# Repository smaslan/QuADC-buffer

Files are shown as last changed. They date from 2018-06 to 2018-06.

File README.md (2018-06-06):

# Precision Buffer with Low Input Capacitance

Following project is a precision buffer developed in scope of project EMPIR project QuADC (see documentation.pdf for details).

The main goal was flatness below 0.1 µV/V up to 10 kHz. Calibration uncertainty at 1 MHz requirement was 5 µV/V. Input capacitance as low as possible. Output impedance as low as possible. The circuit uses bootstrapping of the supply voltages which reduces errors significantly and also ensure very low apparent input shunting capacitance. Cost for the solution is limited stability. The buffer cannot be supplied from low impedance source otherwise it tends to oscillate. It designed as output bufffer for the resistive voltage dividers.

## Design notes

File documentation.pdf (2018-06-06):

## Report on the bootstrapped buffer for QuADC EMPIR

V1.1, 2018-06-06, Czech Metrology Institute, Stanislav Mašláň, smaslan@cmi, s.maslan@seznam.cz

Copyright 2017, Stanislav Mašláň.

This documentation describes Open Hardware and is licensed under the CERN OHL v. 1.2. You may redistribute and modify this documentation under the terms of the CERN OHL v.1.2. (http://ohwr.org/cernohl). This documentation is distributed WITHOUT ANY EXPRESS OR IMPLIED WARRANTY, INCLUDING OF MERCHANTABILITY, SATISFACTORY QUALITY AND FITNESS FOR A PARTICULAR PURPOSE. Please see the CERN OHL v.1.2 for applicable conditions.

### Introduction

Following document briefly describes buffer developed for the EMPIR project QuADC [3]. Main requirement was flatness below 0.1 µV/V up to 10 kHz. Calibration uncertainty at 1 MHz requirement was 5 µV/V. Input capacitance as low as possible. Output impedance as low as possible.

### Basic parameters

Parameter | Value
Supply voltage | (±13.5 up to ±15.5) V
Supply current | < 100 mA, plus fan current in positive supply
Input voltage range | 1.5 Vpk
Input capacitance | < 1 pF
Input DC resistance | 100 MΩ
Output impedance |Z| | < 4 mΩ up to 10 kHz < 12 mΩ up to 100 kHz < 150 mΩ up to 1 MHz
Output inductance | < 20 nH
Flatness | < 0.1 µV/V up to 10 kHz < 2 µV/V up to 100 kHz < 100 µV/V up to 1 MHz (depends on the cable and load)
Estimated THD | < 140 dB up to 100 kHz (10 harmonics) < 106 dB up to 1 MHz (bw. 6 MHz)

### Description

It is derived from the Ilya Budovsky design [1]. Problem of the Budovsky-like designs is there are no feedbacks from the bootstrapped supply rails so the accuracy of them is low. Multi-staging the topology has no significant effect as each following stage is still limited by the finite speed of the floating rail drivers. Furthermore the input capacitance of that design is relatively high.

In the new design, all amplifiers are supplied from the bootstrapped rails so apparent input capacitance is near zero. Also, the printed circuit board (PCB) was designed with 4-layers with careful guarding, so the capacitance is further reduced. The whole board’s apparent input capacitance without connectors is below 1 pF.

Principle of the buffer is shown the Figure 1. For full circuit diagram see Figure 13 or Eagle files. Simplified diagram is shown in Figure 2.

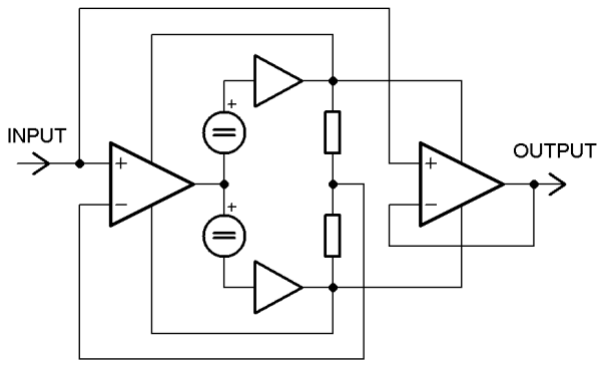
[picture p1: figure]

Figure 1 - Priniciple of operation.

The trick is the feedback took from the bootstrapped rails back to the first stage. The feedback drastically reduces error of the rails to less than 1 % at 1 MHz. The feedback has one more effect. It reduces THD of the rails at low frequencies.

Another trick is the first stage OA is supplied from the floating rails as well. This has two effects. First, it improves the accuracy, same as for the last stage, because the OA only amplifies difference between its supply (common mode voltage) and input. Second, the common mode voltage is following the input, so the apparent input voltage is almost zero. Therefore, the apparent input common mode capacitance is also almost zero.

Problem of this topology is to make it stable. There is a large capacitance between the output/guard and input. PCB guarding has capacitance, OAs have differential capacitance and so on. This large capacitance is basically positive feedback from the output to the input. If the output or guard contain resonant overshoot, it will inevitably lead to the oscillations. So the goal is to properly dump the guard driver so it has low overshoot but at the same time is as fast as possible. Otherwise the apparent input impedance will fall quickly with the frequency. It is also not easy to find feedback RC values to make it stable. Presented circuit was built in two prototypes and it seems repeatable with the listed components, but it does not mean it cannot be improved. For details on the tweaking of the component values see the list of components.

Regarding the stability, I often observed it became unstable if the input is connected to a low impedance source. The input can be shorted directly at the connector. However, when shorted via long coax cable, which acts as a resonator, it will start oscillating easily. It seems to be stable with resistive source as long it has at least few Ohms even via longer cables. It may be made stable using RC snubber network connected to the input or at least to the other side of the input cable, but of course for a cost of a higher input capacitance which will be frequency dependent. On the other hand the output may be loaded by 1 m coax with no observed effects on stability.

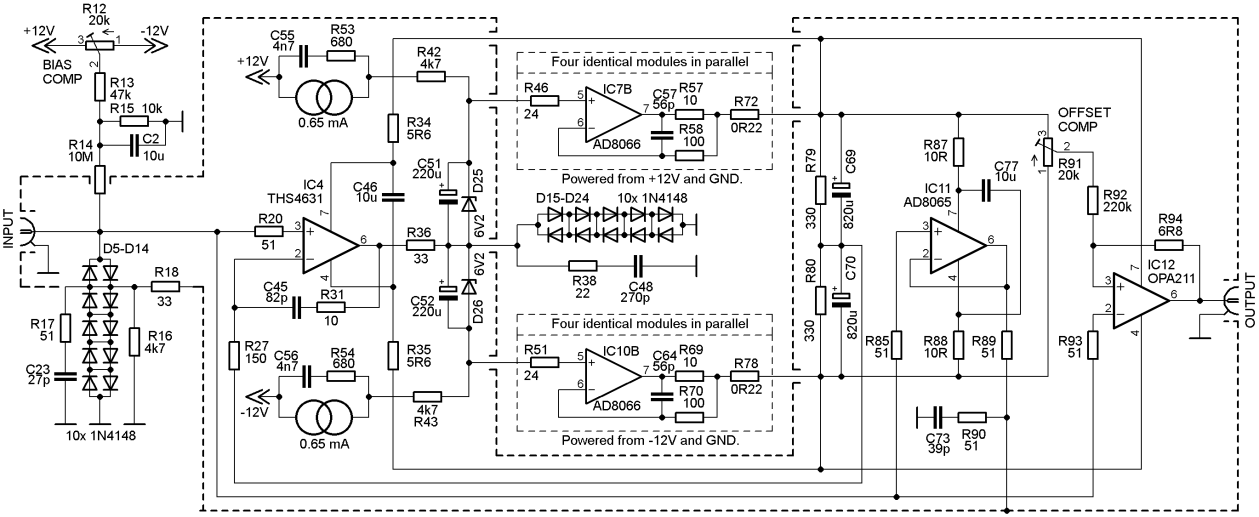
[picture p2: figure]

Figure 2 - Simplified circuit diagram.

Regarding the PCB, it was designed to be small so it fits into the box Hammond HA1455K1602. Board is mounted on 10mm long M3-M3 spacers. Input and output connectors are N-type mounted on sides of the box and soldered directly to the PCB. Note the shields of the connectors has to be connected to the PCB via copper stripes in order to reduce series impedance. Input connector has also prepared solder pads for guard shield, see Figure 10.

The components that needs to be trimmed are placed in the 2.54 mm sockets. Example is shown in the Figure 3. It is ordinary precision socket with round contacts. It can perfectly hold 0207 or 0204 resistors or RM2.5 capacitors. I decided to use this for fine tuning rather than soldering.

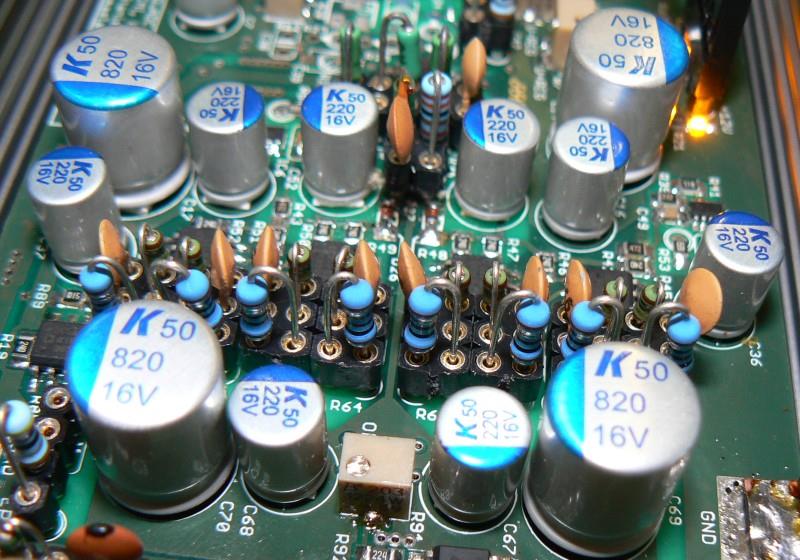
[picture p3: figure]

Figure 3 - 0207 components in the 2.54 mm sockets.

The board also contains lot of unassembled poles and zeroes for tweaking the frequency response. It turned out these are not critical so I did not even tried those, see list of components for instructions.

The buffer prototype was equipped with small 35 mm, 12 V fan running at lower voltage. The fan is probably not needed, but it shortens the heat-up period so I guess it won’t do any harm.

### Components list

component | type | Note
R1 | Trimmer Bourns 3214W, 50k | Negative supply level – multi-turn type!
R2 | 0805, 220k
R3 | 0805, 68k | Negative supply current limiter
R4 | 0805, 510R
R5 | 0805, 2k
R6 | Trimmer SMD 3364W, 2k2 | Fan voltage
R7 | 0805, 110k
R8 | Trimmer Bourns 3214W, 20k | Positive supply level – multi-turn type!
R9 | 0805, 680R | Positive supply current limit
R10 | 0805, 330k
R11 | 0805, 10k
R12 | Trimmer Bourns 3214W, 20k | Bias compensation – multi-turn type!
R13 | 0805, 47k
R14 | 0805, 10M | Input shunt resistor – low Cp, rather low TCR
R15 | 0805, 10k
R16 | 0805, 4k7
R17 | 0207, 51R | 0207 in socket 2.54mm
R18 | 0805, 33R
R19 | 0805, 24R | Dumping resistor, may be increased
R20 | | Not used
R21 R22 | 0805, 2k7
R23, R24, R25 | | Not used
R26 | 0207, 0R0 | 0207 in socket 2.54mm, critical for stability – may be changed
R27 | 0207, 150R | 0207 in socket 2.54mm, critical for stability – may be changed
R28 | | Not used
R29 | 0805, 24R | Dumping resistor, may be increased
R30 | | Not used
R31 | 0805, 10R | 0207 in socket 2.54mm, critical for stability – may be changed
R34, R35 | 0805, 5R6 | May be worthy to fiddle the value for better step response
R36 | 0207, 33R | 0207 in socket 2.54mm, critical for stability – may be changed
R37 | | This is empty socket 2.54mm. Preferably this should be used for exchangeable R38+C48 combination instead of assembling them in SMD. Critical for stability – may be changed
R38 | 0805, 270p | See R37!
R39, R40 | 0805, 3k3

R41 | 0805, 51R
R42, R43 | 0805, 4k7
R44 | 0805, 51R
R45 – R52 | 0805, 24R | Dumping resistors.
R53, R54 | 0207, 680R | 0207 in socket 2.54mm, may affect response
R55, R57, R59, R61 R63, R65, R67, R69 | 0207, 10R | 0207 in socket 2.54mm, may be useful to fiddle with the value for better step response of the bootstrapped rails.
R56, R58, R60, R62 R64, R66, R68, R70 | 0207, 100R | 0207 in socket 2.54mm, may be useful to fiddle with the value for better step response of the bootstrapped rails.
R71 – R78 | 1210, 0R22 | Dumping resistors, low ESL, must be there to prevent IC7 to IC10 “kicking” each other. May be useful to tweak the values.
R79 – R82 | 0805, 680R
R83 | | Not used
R84 | 0207, 10R | Optional, just when bootstrapped voltage needs to be monitored.
R85 | 0805, 51R | Dumping resistor.
R86 | | Not used
R87, R88 | 0805, 10R | May be tweaked for lower overshoot of guard driver.
R89 | 0805, 51R | Guard driver dumping resistor
R90 | 0805, 51R | Part of guard snubber.
R91 | Trimmer Bourns 3214W, 20k | Output offset compensation – multi-turn type!
R92 | 0805, 220k
R93 | 0808, 51R | Dumping resistor, may be increased for better step response.
R94 | 6R8 | Put 0805, 100nF on top of it.
C1, C2, C14, C15, C69, C70 | RM5, D10.5mm, 820uF, 16V, polymer | Maybe 25V type is better, but it’s too big…
C7, C13, C16, C17, C36, C37, C51, C52, C67, C68 | RM2.5, D7mm, 220uF, 16V, polymer | Input ones maybe 25V type is better, but it’s too big…
C11 | 1210, 22uF/16V, ceramic X7R
C3, C4, C20, C26 – C33, C46, C54, C55, C74, C75, C77 | 1210, 10uF/25V, ceramic X7R
C5, C6, C8 – C10, C12, C18, C19, C21, C22, C24, C25, C34, C35, C47, C49, C50, C53, C54, C65, C66, C71, C72, C78 | 0805, 100nF, ceramic X7R | >25V

C23 | THT 2.5mm, 27p, ceramic NP0 | In socket 2.54mm. Tweak for low overshoot.
C43 | | Not used
C48 | 0805, 270p, ceramic NP0 | Tweak for stability. See R37!
C55, C56 | THT 2.5mm, 4n7, ceramic NP0 | In socket 2.54mm, may affect LF response
C38 – C42 | | Not used
C44 | Johanson C-trimmer 9343, 30pF | May not be necessary, may be tweaked by C45 only.
C45 | THT 2.5mm, 82pF, ceramic NP0 | In socket 2.54mm, critical for stability. Tweak for stability and optimal response.
C57 – C64 | THT 2.5mm, 56pF, ceramic NP0 | In socket 2.54mm, may be useful to tweak the value for better bootstrapped rails step response.
C76 | | Not used.
C79 | THT 2.5mm, 39pF, ceramic NP0 | In socket 2.54mm. Tweak for low overshoot on guard.
L1, L2 | Inductor, L3225M, 22uH
D1, D2 | DO214, 1N4007 | May be replaced by 16V+ TVS. Just protection.
D3, D4 | BAT43, Mini-MELF, Schottky | Critical! Without these the positive LDO may get stucked in negative voltage on startup!
D5 – D14 | 1N4148, uMELF | Input ESD protection.
D15 – D24 | 1N4148, uMELF | These are critical to keep inputs of IC7 to IC10 in safe operating range! May be necessary to short one of those five stages (lower input voltage range but more stable).
D25, D26 | Mini-MELF, 6V2 Zener
LD1, LD2 | 0603 LED
IC1 | LM317LD, SO8 | Voltage regulator for fan.
IC2 | LT3042, MSE Package | Positive LDO, don’t forget solder heat pad!
IC3 | LT3090, MSE Package | Negative LDO, don’t forget solder heat pad!
IC4 | THS4631, SO8
IC5, IC6 | LT3092, TS8 Package | Current source.
IC7 – IC10 | AD8066, SO8 | Maybe just two of those are necessary, must be tried…
IC11 | AD8065, SO8
IC12 | OPA211, SO8 | Maybe put some thermal paste under to help stabilizing the temperature.
X1 | 3x2.54 screw socket | Supply input.
X2 | BNC, Radiall R141426161 | Do not assemble, just increases capacitance! Just for test purposes.
X3 | BNC, Radiall R141426161 | Monitor of bootstrapped rails.
X4 | BNC, Radiall R141426161 | Monitor of equipotential (guard).

### Measurements

The buffer was characterized for the basic characteristics using modified digital impedance bridge [2]. First, the input impedance was measured. The result without connectors is shown in the Figure 4. The impedance was measured by placing a known impedance in series with the input and observing change in the transfer. Output impedance show in Figure 5 and Figure 6 was measured similarly by connecting known load to the output and observing change in the transfer.

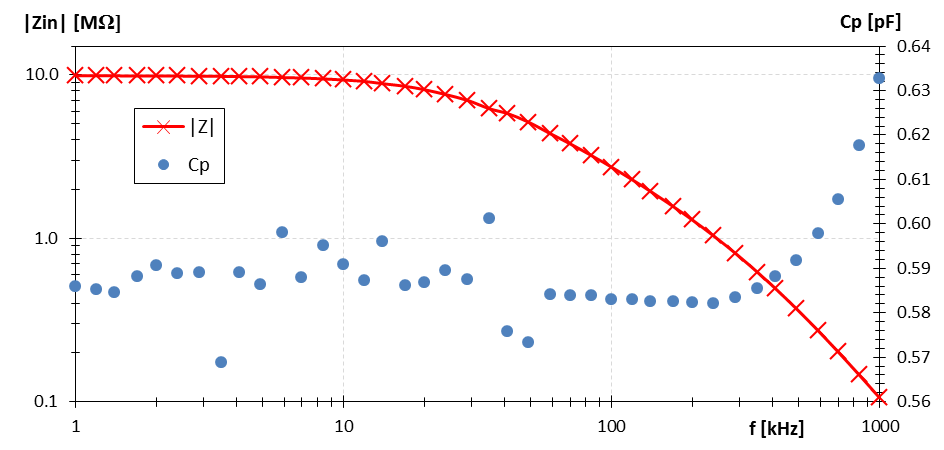
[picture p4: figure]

Figure 4 - Input impedance of the buffer without connector.

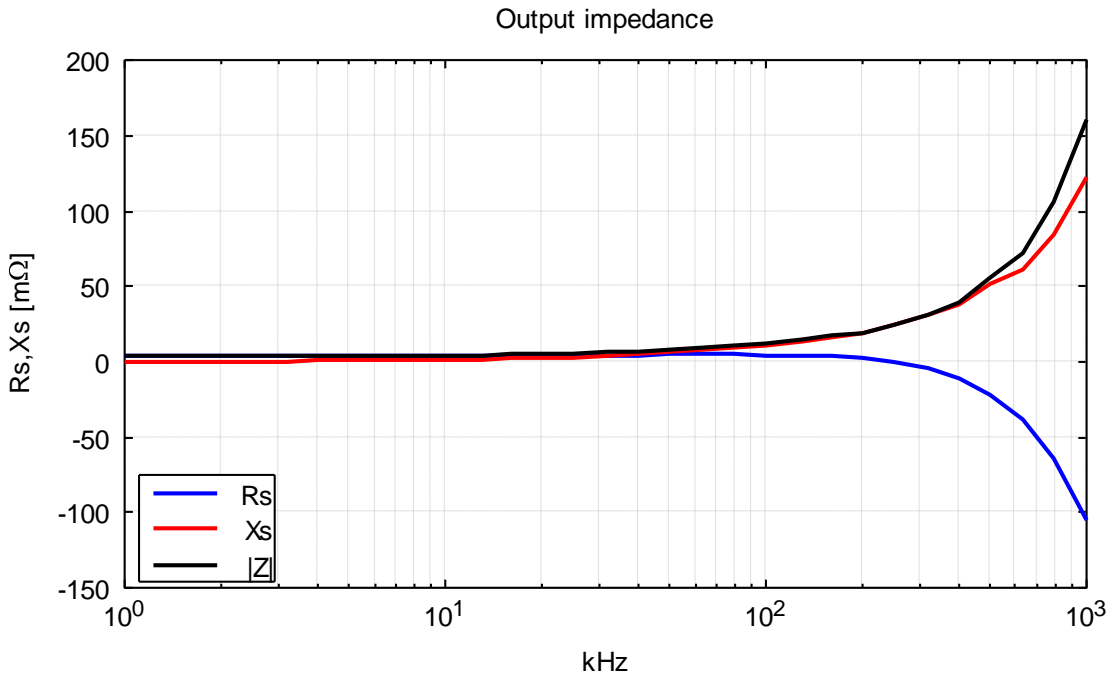
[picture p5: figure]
kHz; Output impedance

Figure 5 - Output impedance with N connector.

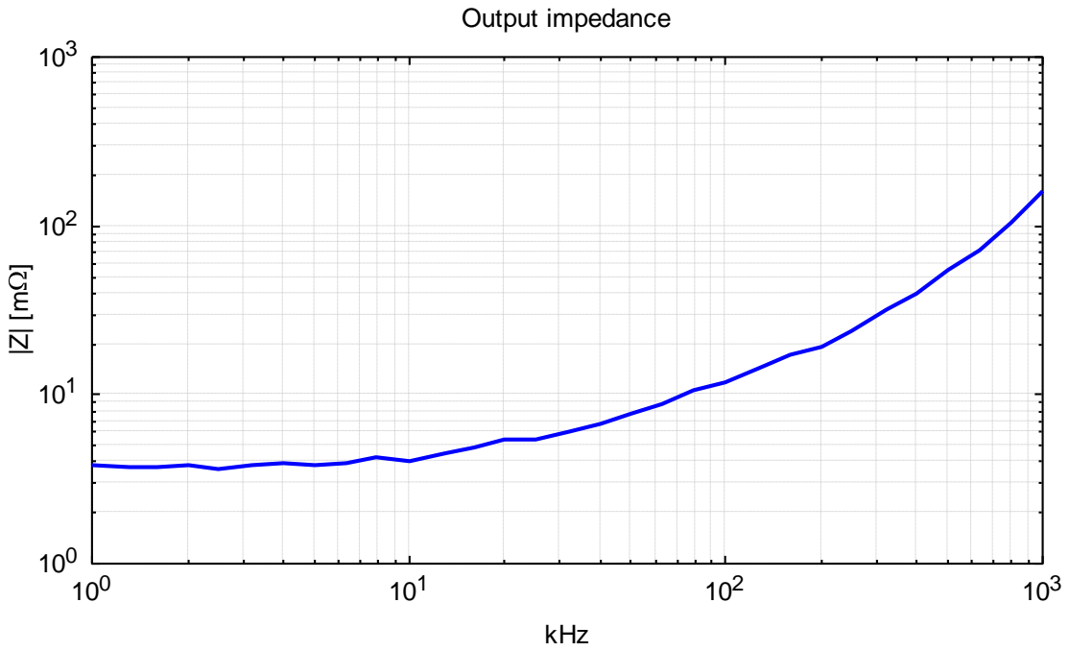
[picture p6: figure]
kHz; Output impedance

Figure 6 - Output impedance with N connector (modulus).

Complex transfer was measured indirectly using the impedance bridge. The raw transfer was then recalculated for apparent no load of the output of the buffer using measured loading impedance of the bridge input and output impedance of the buffer. Then it was virtually loaded by the model of the cable based on its impedance characterization and the desired load. The result is shown in the Figure 7 and Figure 8. Direct measurement was not possible due to the specific load impedance.

Before it will be used for the quantum voltmeter it will have to be done this way as well, as the impedance of the system may differ from the buffer measurement condition. The method was validated by varying the load impedance, observing the changes in transfer and calculating the differences.

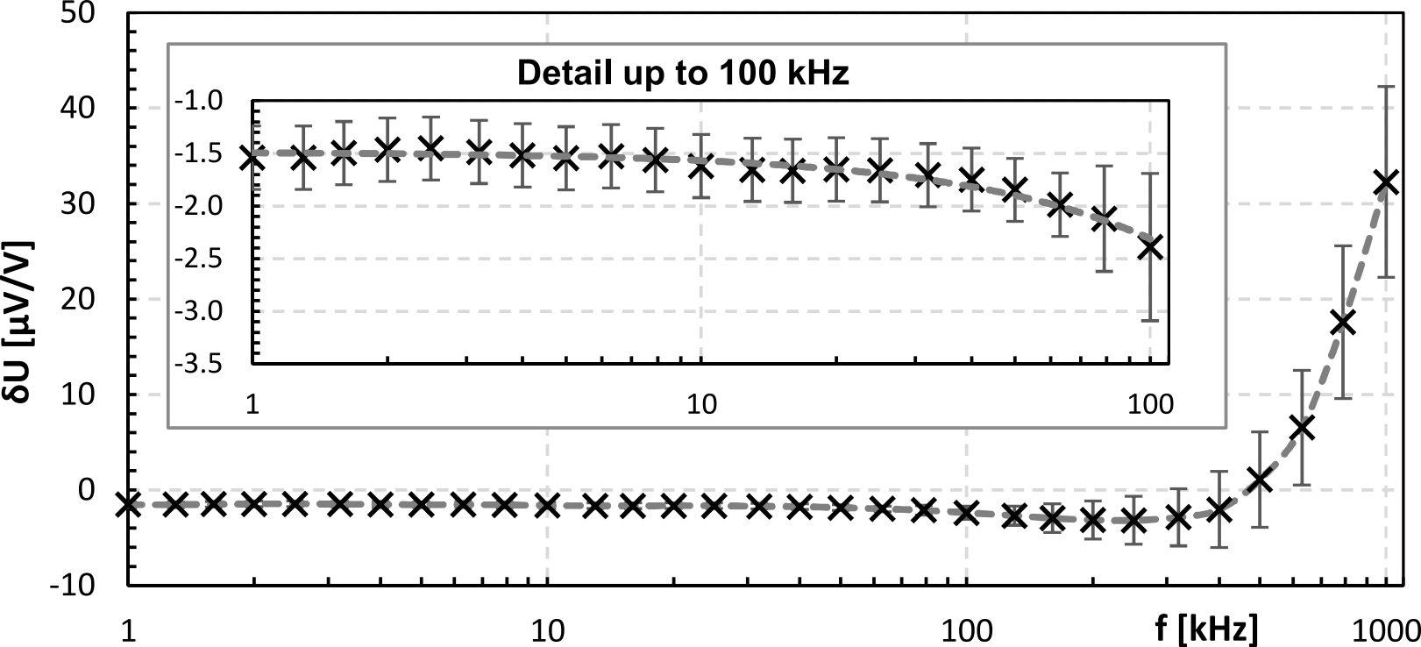
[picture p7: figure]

Figure 7 - Amplitude transfer of the buffer with (10 kΩ || 10pF) load via 20 cm coax cable RG318. Output was measured on the load. Note the amplitude drop -1.5 µV/V is caused by the load resistance and output resistance. The small fluctuations in the gain are caused by insufficient zeroing of the complex ration measurement setup.

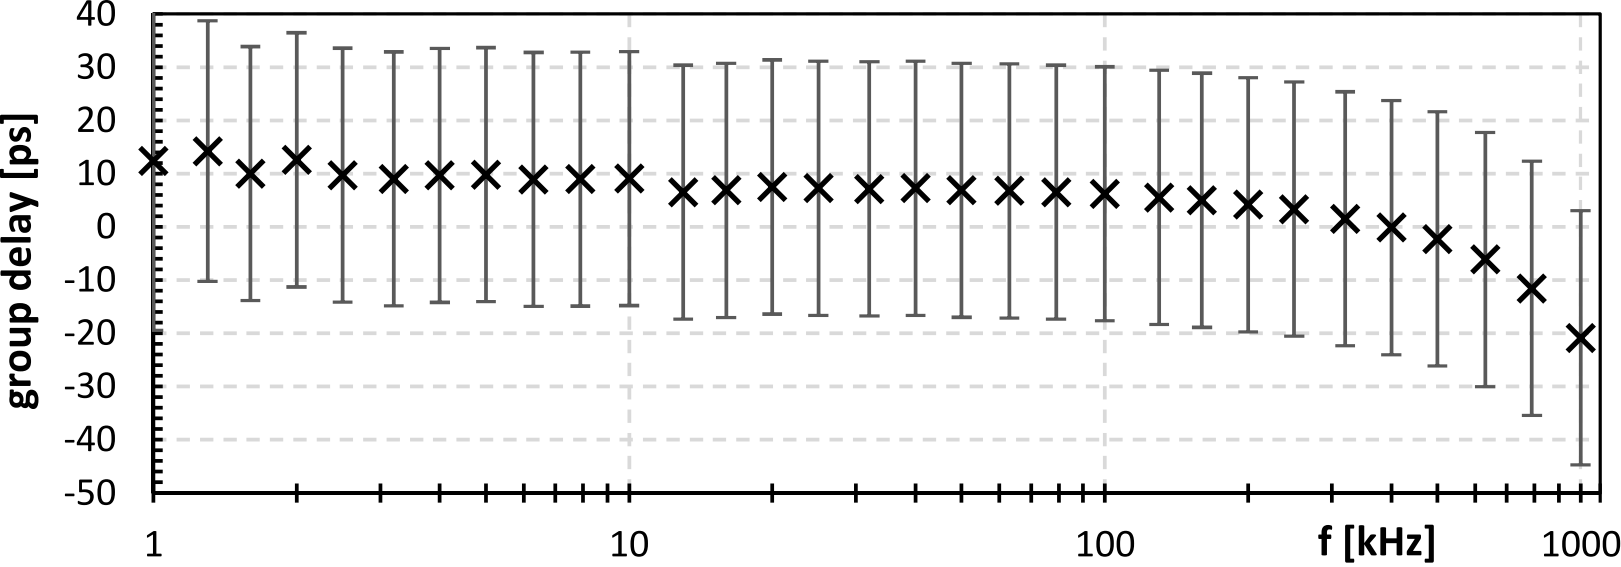
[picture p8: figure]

Figure 8 – Group delay of the buffer with (10 kΩ || 10pF) load via 20 cm coax cable RG318. Output was measured on the load. Note the amplitude drop -1.5 µV/V is caused by the load resistance and output resistance. The small fluctuations in the gain are caused by insufficient zeroing of the complex ration measurement setup.

The THD of the buffer was also measured by the digital impedance bridge setup. The ratio setup measured directly ratio of the input and output harmonics. From the differences it was possible to calculate the THD. It required up to few tens of minutes of total integration time to get stable. Results are < 140 dB up to 100 kHz and < 106 dB at 1 MHz. The 1 MHz value is really just an estimate. No validation was done at this frequency. It is likely the THD is actually much lower.

### Acknowledgement

The buffer was developed in scope of the QuADC project (15SIB04). The project received funding from the EMPIR programme co-financed by the Participating States and from the European Union's Horizon 2020 research and innovation programme. The paper reflects only the author's view and EURAMET is not responsible for any use that may be made of the information it contains.

### References

[1] I. Budovsky and T. Hagen, "A precision buffer amplifier for low-frequency metrology applications," CPEM 2010, Daejeon, 2010, pp. 28-29.
doi: 10.1109/CPEM.2010.5544183
URL: http://ieeexplore.ieee.org/stamp/stamp.jsp?tp=&arnumber=5544183&isnumber=5543133
[2] S. Mašláň, M. Šíra, V. N. Zachovalová and J. Streit, "Digital Sampling Setup for Measurement of Complex Voltage Ratio," in IEEE Transactions on Instrumentation and Measurement, vol. 66, no. 6, pp. 1355-1363, June 2017.
doi: 10.1109/TIM.2017.2649899
URL: http://ieeexplore.ieee.org/stamp/stamp.jsp?tp=&arnumber=7836310&isnumber=7924433
[3] EMPIR project QuADC, URL: https://www.ptb.de/empir/quadc-project.html

### Images

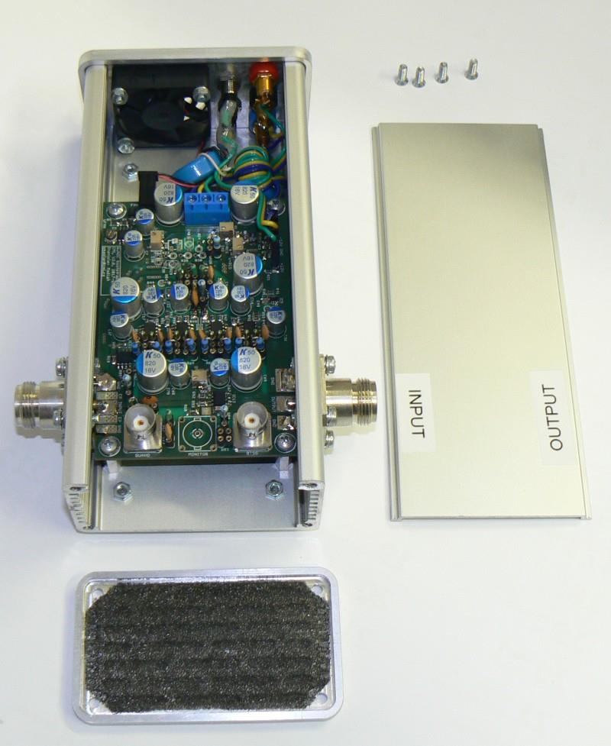
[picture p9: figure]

Figure 9 - Enclosure opened.

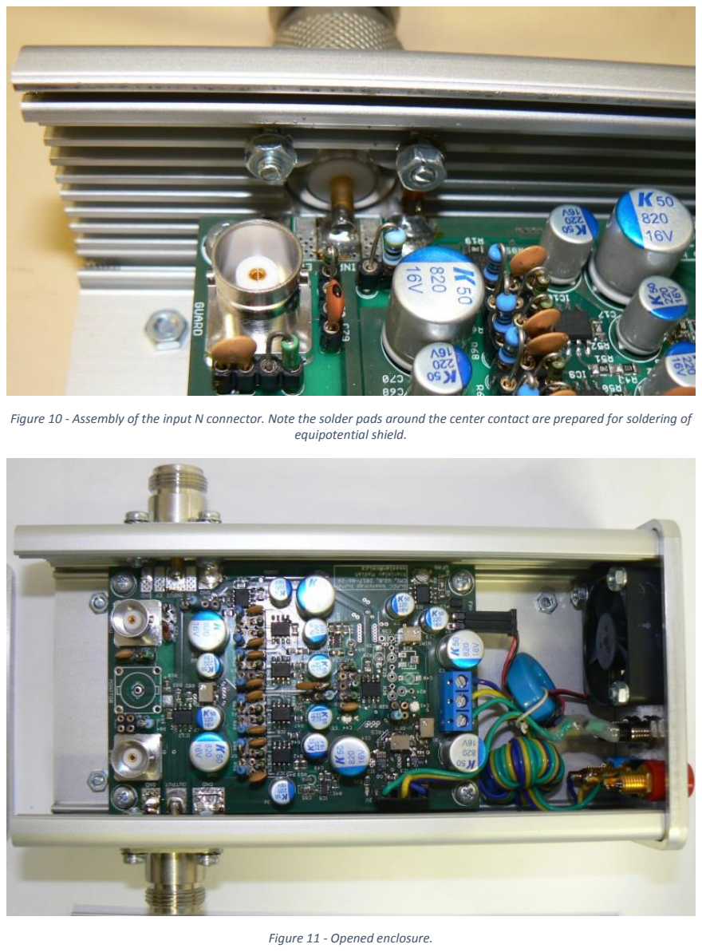
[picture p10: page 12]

Figure 10 - Assembly of the input N connector. Note the solder pads around the center contact are prepared for soldering of equipotential shield.

Figure 11 - Opened enclosure.

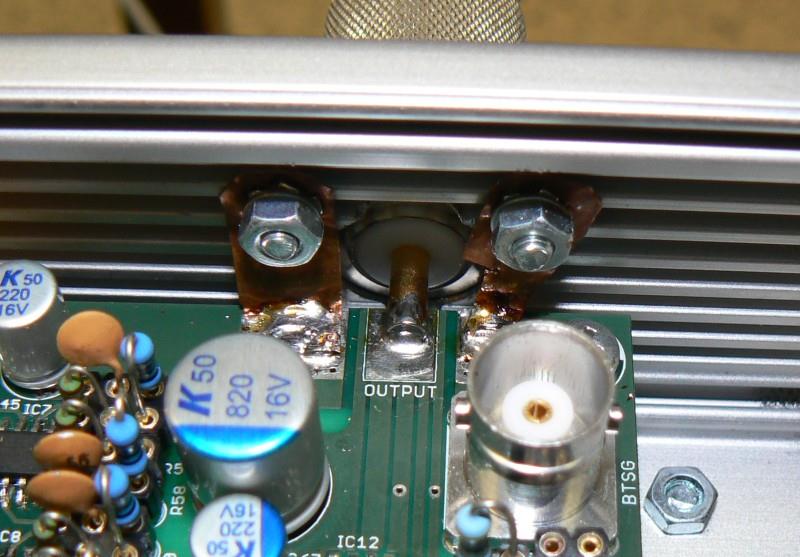
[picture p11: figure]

Figure 12 - Output N connector assembly.

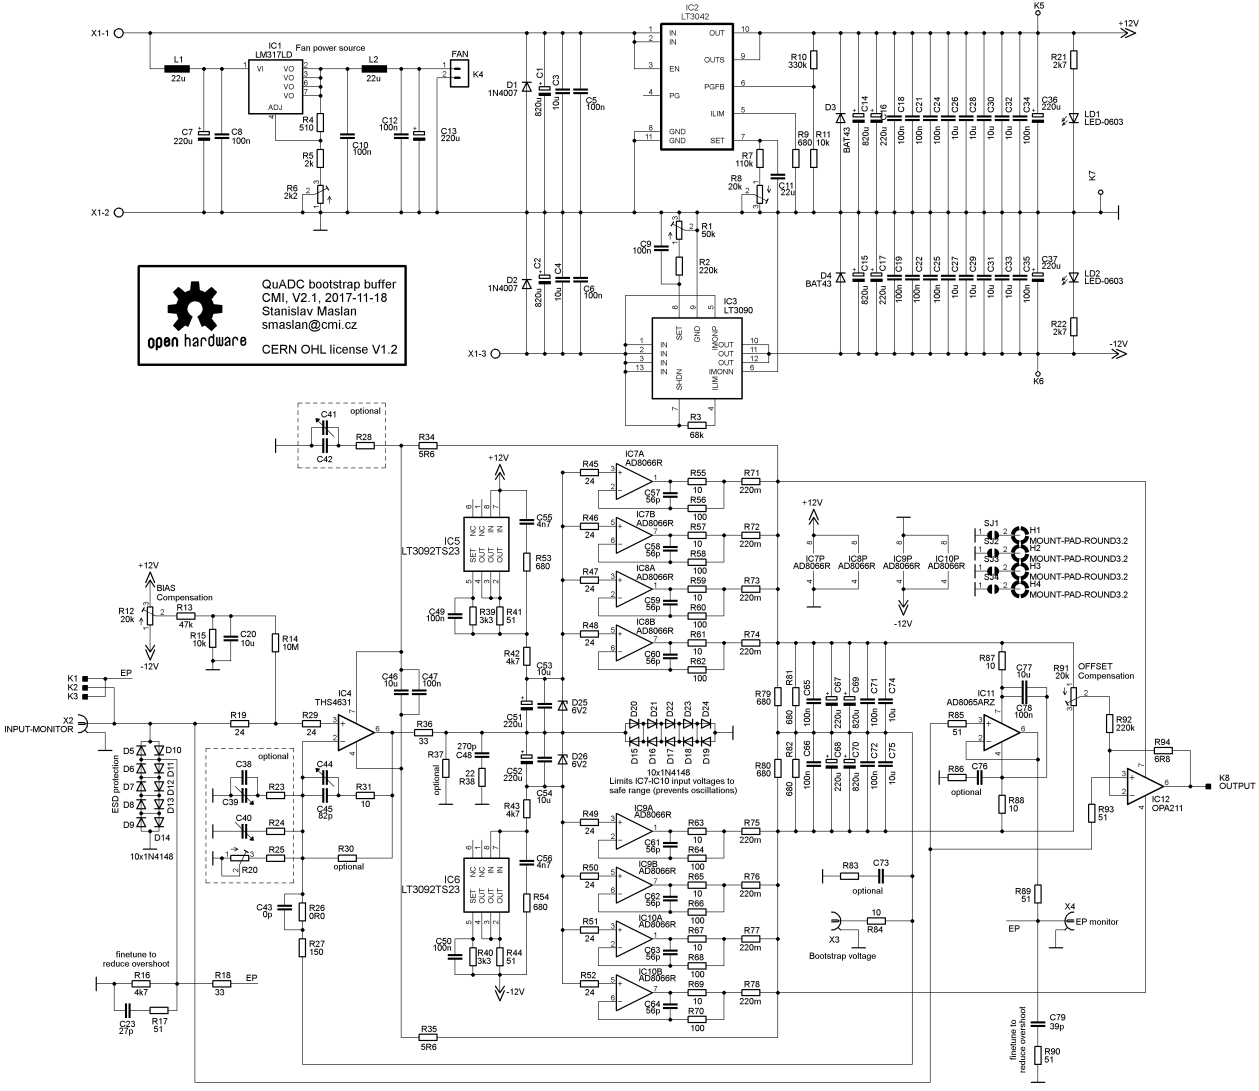
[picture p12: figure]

Figure 13 - Full circuit diagram.

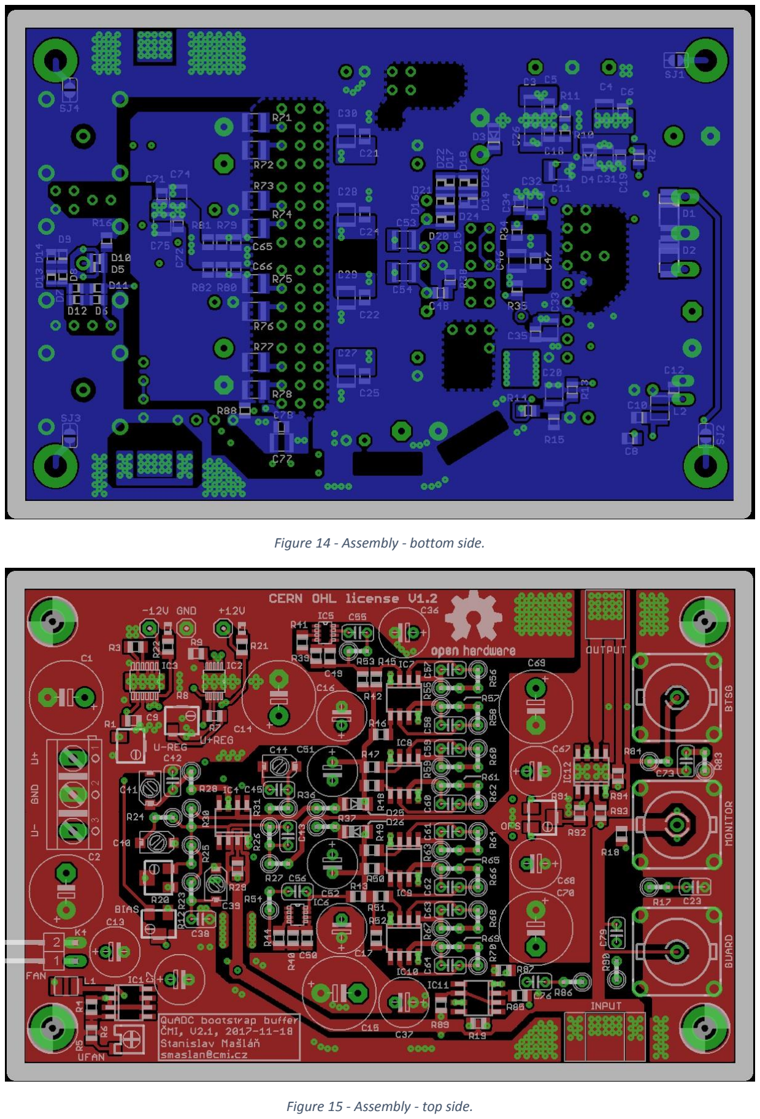
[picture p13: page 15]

Figure 14 - Assembly - bottom side.

Figure 15 - Assembly - top side.

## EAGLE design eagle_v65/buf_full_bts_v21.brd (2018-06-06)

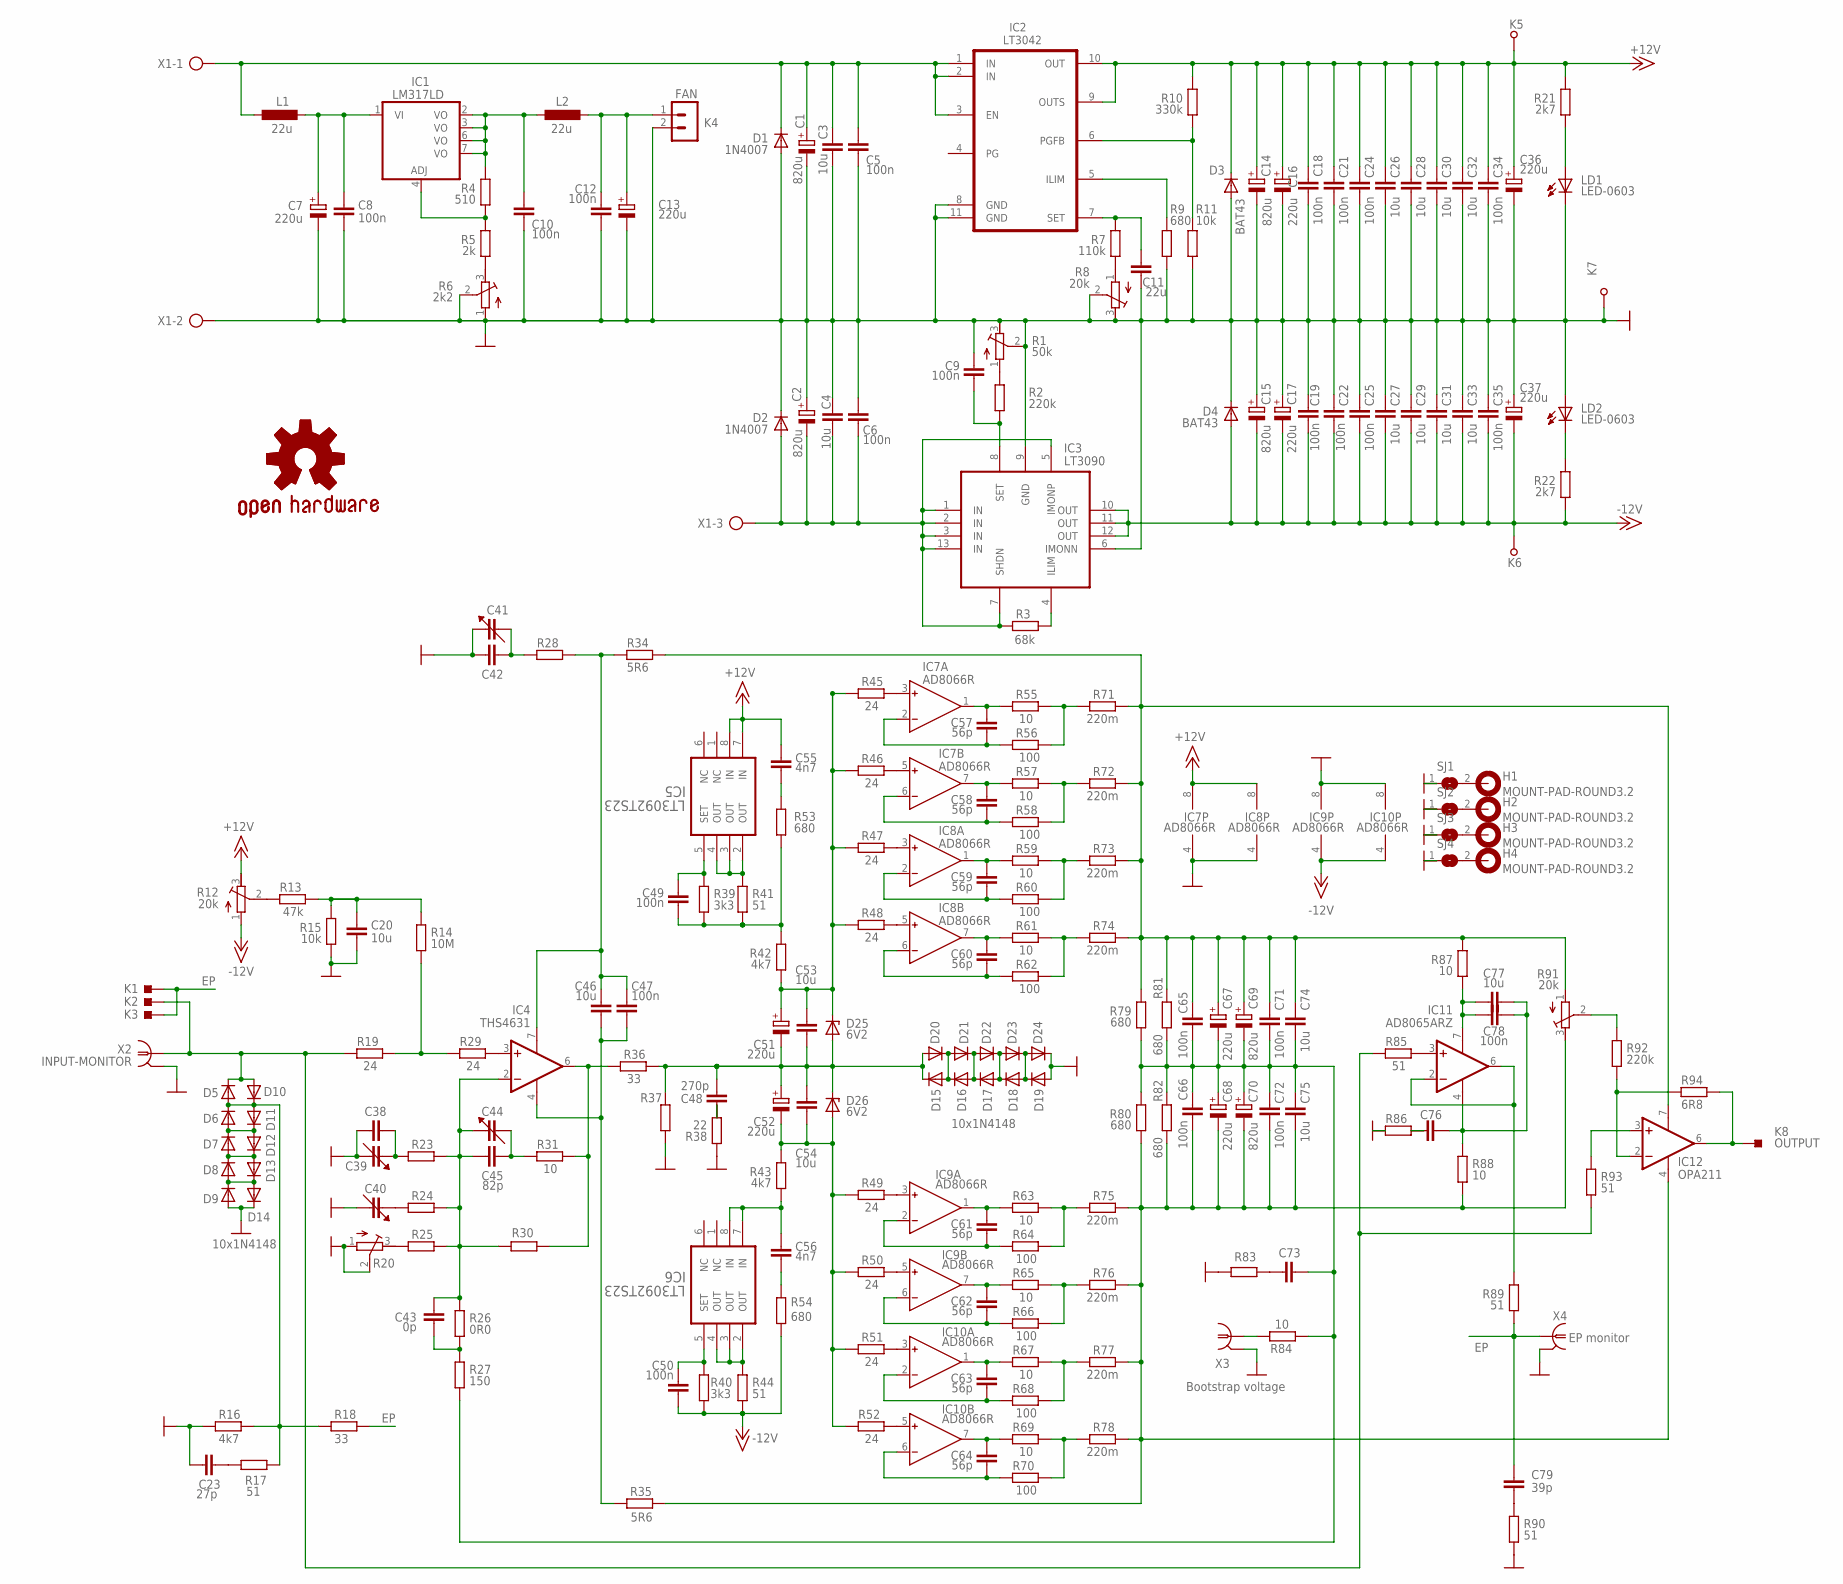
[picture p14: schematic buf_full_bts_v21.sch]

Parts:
C1, C2, C14, C15, C69, C70: 820u; E5-10,5
C3, C4, C20, C26, C27, C28, C29, C30, C31, C32, C33, C46, C53, C54, C74, C75, C77: 10u; C1210K
C5, C6, C8, C9, C10, C12, C18, C19, C21, C22, C24, C25, C34, C35, C47, C49, C50, C65, C66, C71, C72, C78: 100n; X0805
C7, C13, C16, C17, C36, C37, C51, C52, C67, C68: 220u; E2,5-7
C11: 22u; C1210K
C23: 27p; C025-024X044
C38, C42, C73, C76: C-EU025-024X044; C025-024X044
C39, C40, C41, C44: C_TRIMMER-9344; CTRIMMER9344
C43: 0p; C025-024X044
C45: 82p; C025-024X044
C48: 270p; X0805
C55, C56: 4n7; C025-024X044
C57, C58, C59, C60, C61, C62, C63, C64: 56p; C025-024X044
C79: 39p; C025-024X044
D1, D2: 1N4007; DO-214AC
D3, D4: BAT43; SOD80C
D5, D6, D7, D8, D9, D10, D11, D12, D13, D16, D17, D18, D19, D20, D21, D22, D23, D24: DIODE-MICROMELF-W; MICROMELF-W
D14, D15: 10x1N4148; MICROMELF-W
D25, D26: 6V2; SOD80C
GOLD_ORB_SM1: OSHWLOGO_GOLD_ORB_MED; OSHW1
H1, H2, H3, H4: MOUNT-PAD-ROUND3.2; 3,2-PAD
IC1: LM317LD; SO08
IC2: LT3042; SOP50P490X110-11N
IC3: LT3090; SOP65P490X110-13N
IC4: THS4631; SO8
IC5, IC6: LT3092TS23; SOT65P280X100-8N
IC7, IC8, IC9, IC10: AD8066R; SO8
IC11: AD8065ARZ; SO8
IC12: OPA211; SO8
K1, K3: SP_RI; SMD_1X1_S9
K2: SP_RH; SMD_1X1_S8
K4: FAN; MA02-1W
K5, K6, K7: SPP; SP_PRO
K8: OUTPUT; SMD_1X1_S8
L1, L2: 22u; L3225M
LD1, LD2: LED-0603; D0603
R1: 50k; RTRIM3214W
R2, R92: 220k; X0805
R3: 68k; X0805
R4: 510; X0805
R5: 2k; X0805
R6: 2k2; RT3364W
R7: 110k; X0805
R8, R12, R91: 20k; RTRIM3214W
R9, R79, R80, R81, R82: 680; X0805
R10: 330k; X0805
R11, R15: 10k; X0805
R13: 47k; X0805
R14: 10M; X0805
R16, R42, R43: 4k7; X0805
R17, R90: 51; 0207/2V
R18: 33; X0805
R19, R29, R45, R46, R47, R48, R49, R50, R51, R52: 24; X0805
R20: R-TRIMM3214W; RTRIM3214W
R21, R22: 2k7; X0805
R23, R24, R25, R28, R30, R37, R83, R86: R-EU_0207/2V; 0207/2V
R26: 0R0; 0207/2V
R27: 150; 0207/2V
R31, R55, R57, R59, R61, R63, R65, R67, R69, R84: 10; 0207/2V
R34, R35: 5R6; X0805
R36: 33; 0207/2V
R38: 22; X0805
R39, R40: 3k3; X0805
R41, R44, R85, R89, R93: 51; X0805
R53, R54: 680; 0207/2V
R56, R58, R60, R62, R64, R66, R68, R70: 100; 0207/2V
R71, R72, R73, R74, R75, R76, R77, R78: 220m; R1210
R87, R88: 10; X0805
R94: 6R8; X0805
SJ1, SJ2, SJ3, SJ4: SJ
X1: AK500/3
X2: INPUT-MONITOR; A1944
X3: Bootstrap voltage; A1944
X4: EP monitor; A1944

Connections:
+15V: C14.+, C16.+, C18.P$1 (1), C21.P$1 (1), C24.P$1 (1), C26.1, C28.1, C30.1, C32.1, C34.P$1 (1), C36.+, C55.1, D3.C, IC2.9 (OUTS), IC2.10 (OUT), IC5.7 (IN), IC5.8 (IN), IC7.8 (V+), IC8.8 (V+), K5.P$1, R10.P$2 (2), R12.3 (E), R21.P$2 (2)
+15V1: C56.1, IC6.7 (IN), IC6.8 (IN), R43.P$1 (1)
+15V2: C1.+, C3.1, C5.P$1 (1), D1.C, IC2.1 (IN), IC2.2 (IN), IC2.3 (EN), L1.1, X1.1
-15V: C15.-, C17.-, C19.P$2 (2), C22.P$2 (2), C25.P$2 (2), C27.2, C29.2, C31.2, C33.2, C35.P$2 (2), C37.-, C50.P$2 (2), D4.A, IC3.10 (OUT), IC3.11 (OUT), IC3.12 (OUT), IC9.4 (V-), IC10.4 (V-), K6.P$1, R12.1 (A), R22.P$1 (1), R40.P$1 (1), R44.P$1 (1), R54.1
-15V1: C2.-, C4.2, C6.P$2 (2), D2.A, IC3.1 (IN), IC3.2 (IN), IC3.3 (IN), IC3.5 (IMONP), IC3.7 (SHDN), IC3.13 (IN), R3.P$2 (2), X1.3
BTS+: C65.P$1 (1), C67.+, C69.+, C71.P$1 (1), C74.1, IC12.7 (V+), R34.P$2 (2), R71.2, R72.2, R73.2, R74.2, R79.P$2 (2), R81.P$2 (2), R87.P$2 (2), R91.1 (A)
BTS-: C66.P$2 (2), C68.-, C70.-, C72.P$2 (2), C75.2, IC12.4 (V-), R35.P$1 (1), R75.2, R76.2, R77.2, R78.2, R80.P$1 (1), R82.P$1 (1), R88.P$1 (1), R91.3 (E)
BTSG: C65.P$2 (2), C66.P$1 (1), C67.-, C68.+, C69.-, C70.+, C71.P$2 (2), C72.P$1 (1), C73.2, C74.2, C75.1, R27.2, R79.P$1 (1), R80.P$2 (2), R81.P$1 (1), R82.P$2 (2), R84.1
EP: C79.2, K1.1, K3.1, R18.P$1 (1), R89.P$1 (1), X4.1
GND: C1.-, C2.+, C3.2, C4.1, C5.P$2 (2), C6.P$1 (1), C7.-, C8.P$2 (2), C9.P$1 (1), C10.P$2 (2), C11.2, C12.P$2 (2), C13.-, C14.-, C15.+, C16.-, C17.+, C18.P$2 (2), C19.P$1 (1), C20.2, C21.P$2 (2), C22.P$1 (1), C23.1, C24.P$2 (2), C25.P$1 (1), C26.2, C27.1, C28.2, C29.1, C30.2, C31.1, C32.2, C33.1, C34.P$2 (2), C35.P$1 (1), C36.-, C37.+, C38.2, C39.2 (1), C40.2 (1), C41.1 (2), C42.1, D1.A, D2.C, D3.A, D4.C, D9.A, D14.C, D19.A, D24.C, IC2.8 (GND), IC2.11 (GND), IC3.6 (IMONN), IC3.9 (GND), IC7.4 (V-), IC8.4 (V-), IC9.8 (V+), IC10.8 (V+), K4.2, K7.P$1, LD1.K (C), LD2.A, R1.2 (S), R1.3 (E), R6.1 (A), R6.2 (S), R8.2 (S), R8.3 (E), R9.P$1 (1), R11.P$1 (1), R15.P$1 (1), R16.P$2 (2), R20.1 (A), R20.2 (S), R37.1, R38.P$1 (1), R83.1, R86.1, R90.1, SJ1.1, SJ2.1, SJ3.1, SJ4.1, X1.2, X2.2, X2.3 (2), X2.4 (2), X2.5 (2), X3.2, X3.3 (2), X3.4 (2), X3.5 (2), X4.2, X4.3 (2), X4.4 (2), X4.5 (2)
IN: D5.C, D10.A, K2.1, R19.P$1 (1), R85.P$1 (1), R93.P$1 (1), X2.1
unnamed: C59.2, IC8.2 (IN-), R60.1
unnamed: C59.1, IC8.1 (OUT), R59.1
unnamed: C60.1, IC8.7 (OUT), R61.1
unnamed: C60.2, IC8.6 (IN-), R62.1
unnamed: R61.2, R62.2, R74.1
unnamed: R59.2, R60.2, R73.1
unnamed: C57.2, IC7.2 (IN-), R56.1
unnamed: C57.1, IC7.1 (OUT), R55.1
unnamed: C58.1, IC7.7 (OUT), R57.1
unnamed: C58.2, IC7.6 (IN-), R58.1
unnamed: R57.2, R58.2, R72.1
unnamed: R55.2, R56.2, R71.1
unnamed: IC7.3 (IN+), R45.P$2 (2)
unnamed: IC7.5 (IN+), R46.P$2 (2)
unnamed: IC8.3 (IN+), R47.P$2 (2)
unnamed: IC8.5 (IN+), R48.P$2 (2)
unnamed: C63.2, IC10.2 (IN-), R68.1
unnamed: C63.1, IC10.1 (OUT), R67.1
unnamed: C64.1, IC10.7 (OUT), R69.1
unnamed: C64.2, IC10.6 (IN-), R70.1
unnamed: R69.2, R70.2, R78.1
unnamed: R67.2, R68.2, R77.1
unnamed: C61.2, IC9.2 (IN-), R64.1
unnamed: C61.1, IC9.1 (OUT), R63.1
unnamed: C62.1, IC9.7 (OUT), R65.1
unnamed: C62.2, IC9.6 (IN-), R66.1
unnamed: R65.2, R66.2, R76.1
unnamed: R63.2, R64.2, R75.1
unnamed: IC9.3 (IN+), R49.P$2 (2)
unnamed: IC9.5 (IN+), R50.P$2 (2)
unnamed: IC10.3 (IN+), R51.P$2 (2)
unnamed: IC10.5 (IN+), R52.P$2 (2)
unnamed: LD2.K (C), R22.P$2 (2)
unnamed: C51.+, C53.1, D25.C, R42.P$1 (1), R45.P$1 (1), R46.P$1 (1), R47.P$1 (1), R48.P$1 (1)
unnamed: C52.-, C54.2, D26.A, R43.P$2 (2), R49.P$1 (1), R50.P$1 (1), R51.P$1 (1), R52.P$1 (1)
unnamed: C48.P$2 (2), C51.-, C52.+, C53.2, C54.1, D15.C, D20.A, D25.A, D26.C, R36.2, R37.2
unnamed: C23.2, R17.2
unnamed: C50.P$1 (1), IC6.5 (SET), R40.P$2 (2)
unnamed: IC4.3 (+IN), R29.P$2 (2)
unnamed: IC4.6 (OUT), R30.1, R31.2, R36.1
unnamed: C46.1, C47.P$1 (1), IC4.7 (V+), R28.2, R34.P$1 (1)
unnamed: IC6.2 (OUT), IC6.3 (OUT), IC6.4 (OUT), R44.P$2 (2)
unnamed: C46.2, C47.P$2 (2), IC4.4 (V-), R35.P$2 (2)
unnamed: C49.P$1 (1), IC5.5 (SET), R39.P$2 (2)
unnamed: C41.2 (1), C42.2, R28.1
unnamed: IC5.2 (OUT), IC5.3 (OUT), IC5.4 (OUT), R41.P$2 (2)
unnamed: C43.2, R26.2, R27.1
unnamed: C49.P$2 (2), R39.P$1 (1), R41.P$1 (1), R42.P$2 (2), R53.1
unnamed: C43.1, C44.1 (2), C45.1, IC4.2 (-IN), R23.1, R24.1, R25.1, R26.1, R30.2
unnamed: IC12.3 (+IN), R93.P$2 (2)
unnamed: C56.2, R54.2
unnamed: C11.1, IC2.7 (SET), R7.P$2 (2)
unnamed: C55.2, R53.2
unnamed: R20.3 (E), R25.2
unnamed: IC12.2 (-IN), R92.P$2 (2), R94.P$1 (1)
unnamed: R91.2 (S), R92.P$1 (1)
unnamed: R7.P$1 (1), R8.1 (A)
unnamed: D7.A, D8.C, D12.C, D13.A
unnamed: D6.A, D7.C, D11.C, D12.A
unnamed: LD1.A, R21.P$1 (1)
unnamed: IC2.6 (PGFB), R10.P$1 (1), R11.P$2 (2)
unnamed: R1.1 (A), R2.P$2 (2)
unnamed: C9.P$2 (2), IC3.8 (SET), R2.P$1 (1)
unnamed: D8.A, D9.C, D13.C, D14.A
unnamed: C20.1, R13.P$2 (2), R14.P$1 (1), R15.P$2 (2)
unnamed: R12.2 (S), R13.P$1 (1)
unnamed: D5.A, D6.C, D10.C, D11.A, R16.P$1 (1), R17.1, R18.P$2 (2)
unnamed: IC3.4 (ILIM), R3.P$1 (1)
unnamed: R84.2, X3.1
unnamed: C40.1 (2), R24.2
unnamed: C38.1, C39.1 (2), R23.2
unnamed: C44.2 (1), C45.2, R31.1
unnamed: C79.1, R90.2
unnamed: C77.1, C78.P$1 (1), IC11.7 (V+), R87.P$1 (1)
unnamed: C73.1, R83.2
unnamed: IC11.3 (+IN), R85.P$2 (2)
unnamed: IC11.2 (-IN), IC11.6 (OUT), R89.P$2 (2)
unnamed: C76.2, C77.2, C78.P$2 (2), IC11.4 (V-), R88.P$2 (2)
unnamed: C76.1, R86.2
unnamed: H1.B3,2, SJ1.2
unnamed: H2.B3,2, SJ2.2
unnamed: H3.B3,2, SJ3.2
unnamed: H4.B3,2, SJ4.2
unnamed: R14.P$2 (2), R19.P$2 (2), R29.P$1 (1)
unnamed: C10.P$1 (1), IC1.2 (VO), IC1.3 (VO), IC1.6 (VO), IC1.7 (VO), L2.1, R4.P$2 (2)
unnamed: IC1.4 (ADJ), R4.P$1 (1), R5.P$2 (2)
unnamed: C48.P$1 (1), R38.P$2 (2)
unnamed: C12.P$1 (1), C13.+, K4.1, L2.2
unnamed: R5.P$1 (1), R6.3 (E)
unnamed: C7.+, C8.P$1 (1), IC1.1 (VI), L1.2
unnamed: D18.A, D19.C, D23.C, D24.A
unnamed: D17.A, D18.C, D22.C, D23.A
unnamed: D16.A, D17.C, D21.C, D22.A
unnamed: D15.A, D16.C, D20.C, D21.A
unnamed: IC2.5 (ILIM), R9.P$2 (2)
OUT: IC12.6 (OUT), K8.1, R94.P$2 (2)

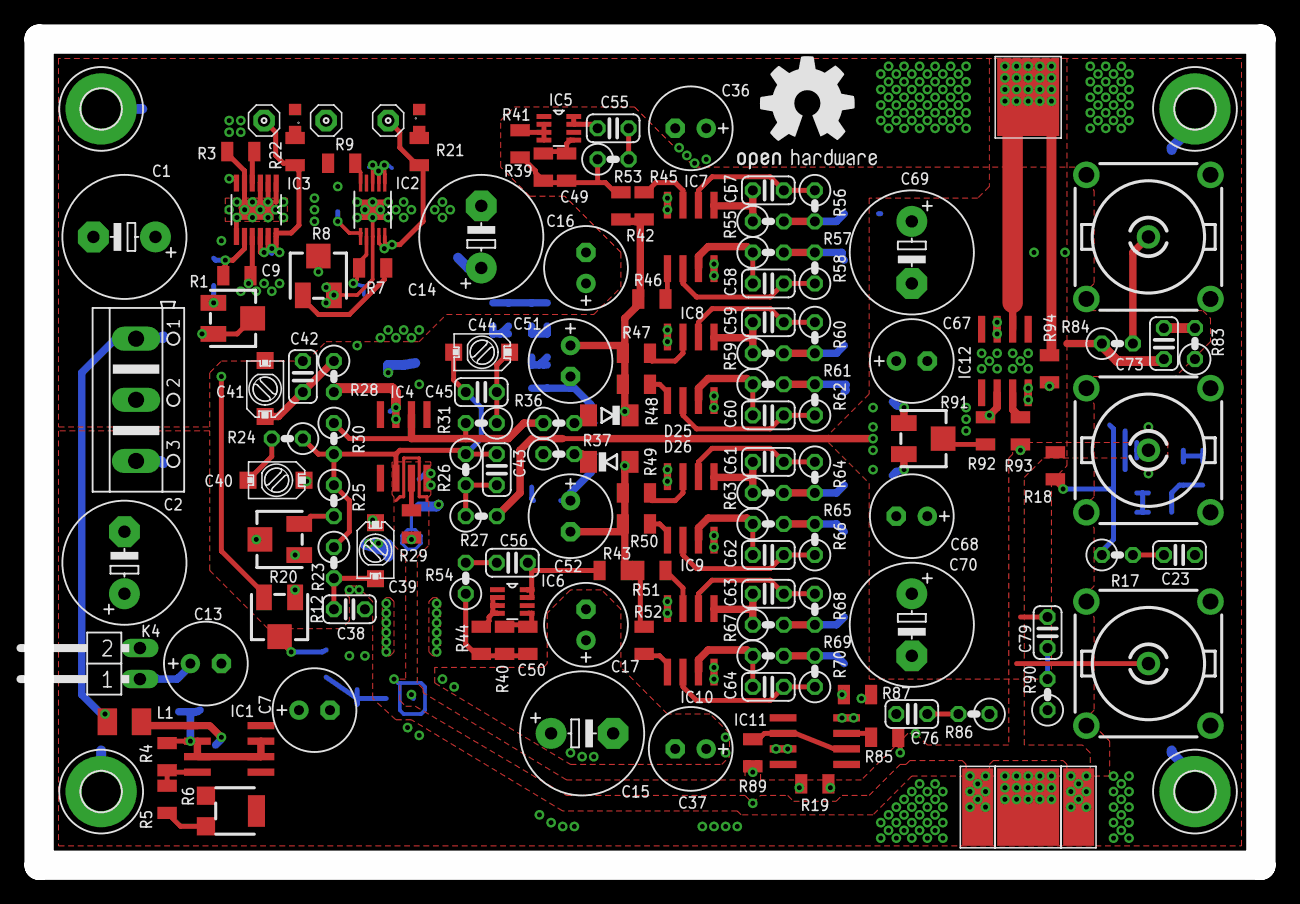
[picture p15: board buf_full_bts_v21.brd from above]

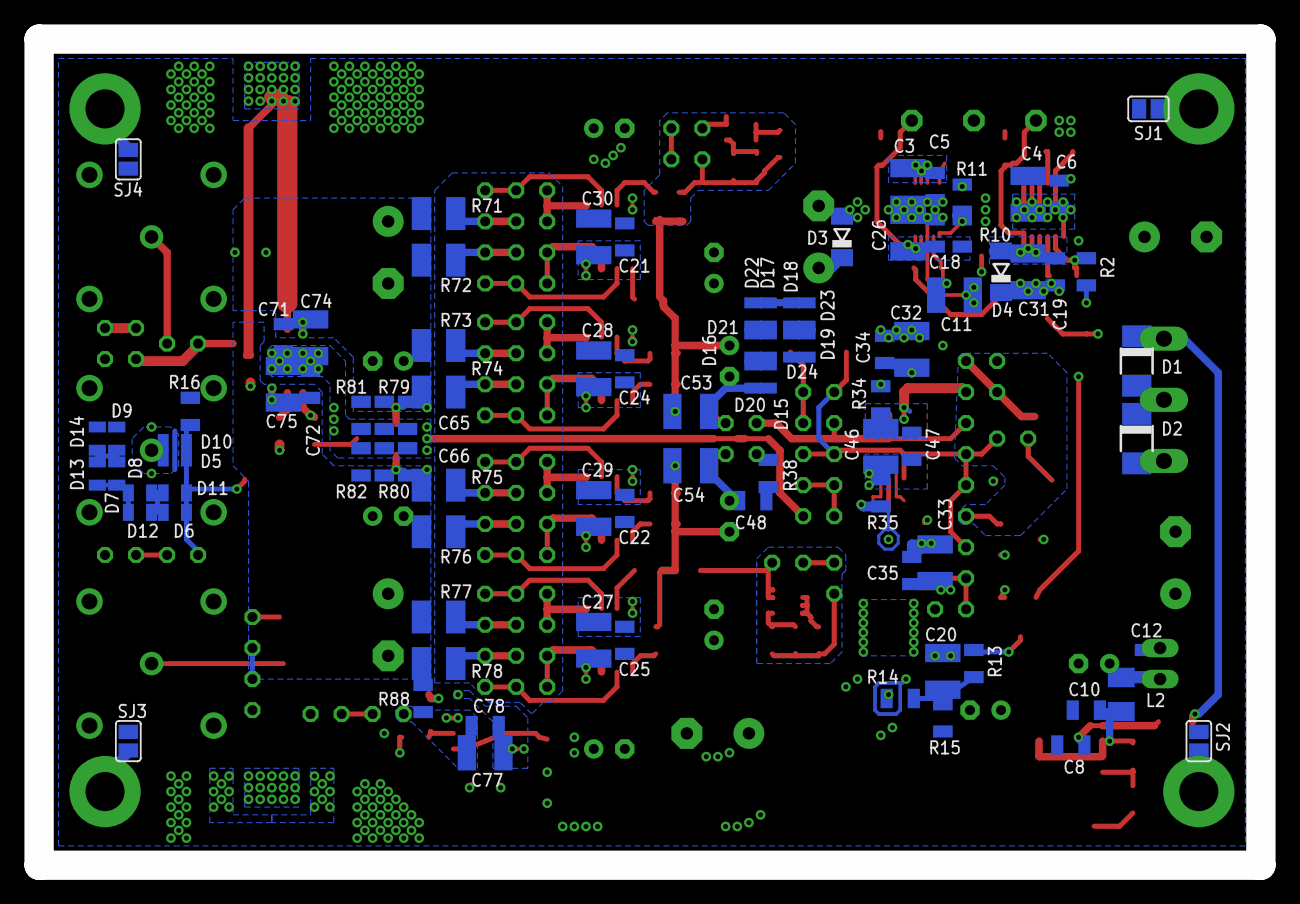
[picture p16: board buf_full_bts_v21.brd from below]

Board: 4 copper layers, 100.0 x 67.6 mm, 234 parts (90 on the bottom side), 107 nets.

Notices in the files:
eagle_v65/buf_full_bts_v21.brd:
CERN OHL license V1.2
